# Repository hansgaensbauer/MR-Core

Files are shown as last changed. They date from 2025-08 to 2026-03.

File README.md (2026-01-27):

### __Quick Start:__ The [software](/software) folder contains a template Jupyter Notebook and documentation for the MRC class. 

# MR-Core
An FPGA Driven DAC + ADC for Magnetic Resonance, intended as a capable controller for Magnetic Resonance Imaging and Magnetic Resonance Relaxometry. 

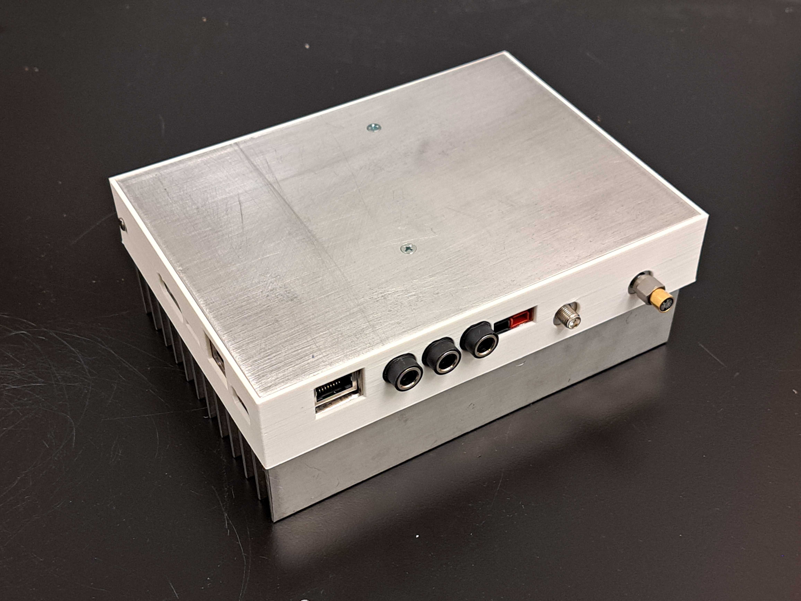
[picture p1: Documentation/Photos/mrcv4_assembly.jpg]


### Features
- STM32F767 Microcontroller for experiment-level sequencing and backend signal processing
- Artix 7 FPGA for pulse generation, digital downconversion and DSP
- 500MSps dual oversampling DAC with on-chip NCO for RF pulse synthesis
- 120MSps dual ADC
- X, Y, and Z gradient drivers for 3A low impedance gradient coils
- 5Gbps USB-3.0 controller for raw data extraction
- 100/10 Ethernet 
- SD Card Interface
- Magnet/switch interface for temperature control and T/R switching

# User Manual

## Repository Setup and Software Prerequisites
### Required Software
- [KiCAD EDA](https://www.kicad.org/)
- [STM32CubeIDE](https://www.st.com/en/development-tools/stm32cubeide.html)
    - [STM32CubeF7 Package](https://www.st.com/en/embedded-software/stm32cubef7.html) Version 1.7.1 or 1.7.2
    - ARM CMSIS 5.4.0
- [AMD Vivado](https://www.xilinx.com/products/design-tools/vivado.html)

</br>
To set up the KiCAD Libraries:

- Open KiCAD, go to Preferences -> Configure Paths..., and add a new Environment Variable called "BioMEMS" that points to the hardware/Library folder. 
- Add the symbol library by selecting Preferences -> Manage Symbol Libraries... and selecting the BioMEMS.kicad_sym file in this folder. 
- Check that the library path shows up as "${BioMEMS}.kicad_sym". 
- Add the footprint library by selecting Preferences -> Manage Footprint Libraries... and selecting the BioMEMS.pretty folder in Library. 
- Check that the library path uses the ${BioMEMS} variable.

</br>
The STM32CubeIDE project requires similar setup:

- Create an environment variable called STM32CUBE_REPO, pointed to the STM32Cube\Repository folder on your computer.
- Restart your computer
- Open the project in STM32CubeIDE, and navigate to the IOC file
- Under "Software Packs", click "Manage Software Packs"
- Click "From URL", then "New"
- Add the URL "https://raw.githubusercontent.com/STMicroelectronics/STM32CubeF7/master/Drivers/CMSIS/ARM.CMSIS.pdsc"
- Click "OK" (several times) to add the software pack.
- You may have to close and reopen the "Manage Software Packs" window
- Click the "ARM" tab, and check "CMSIS 5.4.0"
- Click "OK" to close the window, then click "Select Components" under "Software Packs"
- Expand ARM.CMSIS, and check "CMSIS Core - 5.1.2" and "CMSIS DSP 1.5.2" 
- Click OK
- Under Middleware and Software Packs, click "CMSIS", and make sure both CMSIS Core and DSP are checked in the panel that opens
- Save the IOC and rebuild the code
- To add the STM32CubeF7 repository, extract the STM32CubeF7 to the STM32CUBE_REPO folder (next to "Packs")
- Pull the STM32Cube_FW_F7_V1.17.X folder out so it's at the same level as the Packs folder. Check that the path to this folder matches the include paths in Project->Properties (you may have to rename the folder or adjust the paths).

## Hardware Description
### Open Assembly
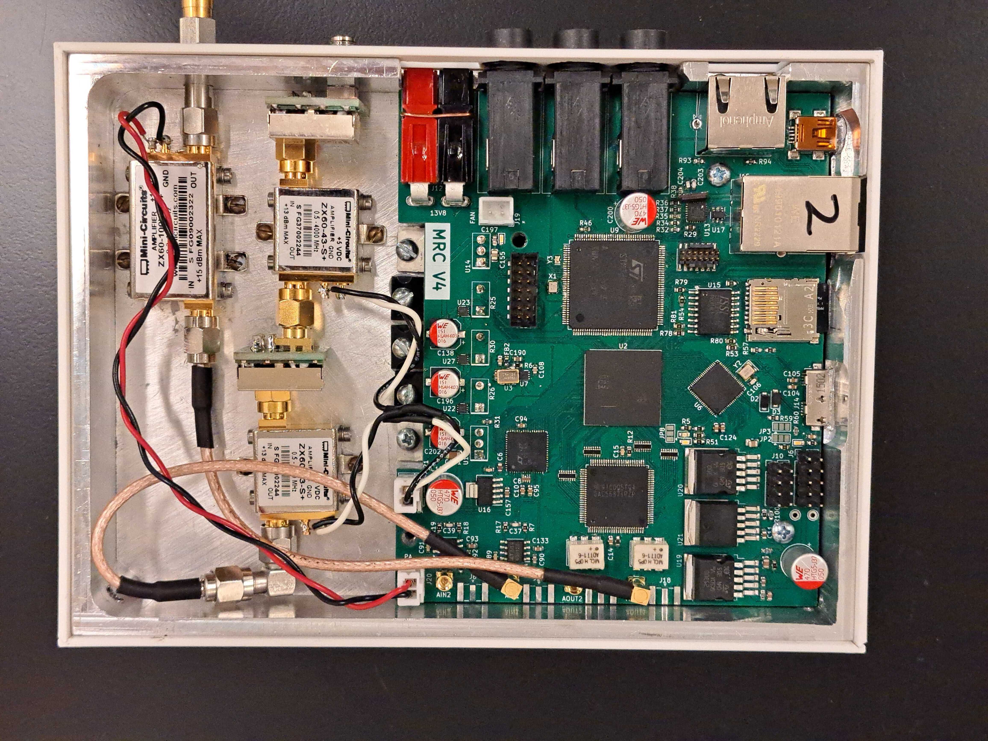
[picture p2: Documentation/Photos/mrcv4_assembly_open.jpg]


### PCB Connector Diagram
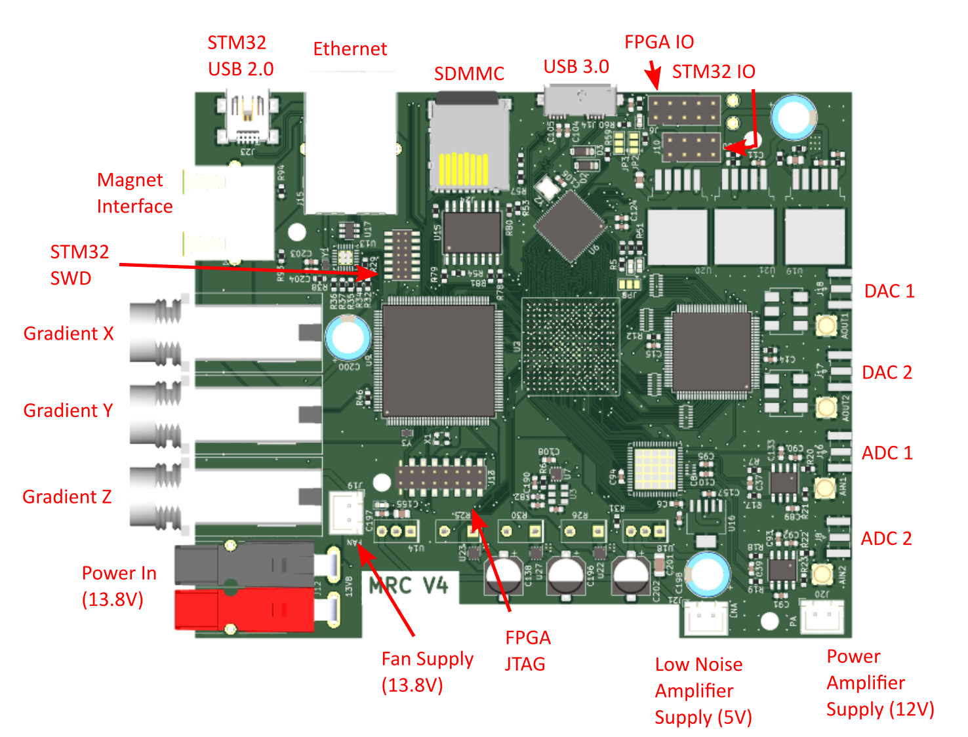
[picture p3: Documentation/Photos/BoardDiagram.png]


## Powering On
The MR-Core is designed to work with a 13.8V DC power supply, such as those sold by [Astron Corporation](https://www.astroncorp.com/). These are commonly used for amateur radio, but any linear power supply capable of providing 10A continuously is suitable. If the gradients are not used, only 3A are required. The power connector is a [ASMPR45-1X2-RK](https://www.digikey.com/en/products/detail/anderson-power-products-inc/ASMPR45-1X2-RK/13150596) from [Anderson Power Products, Inc.](https://www.andersonpower.com/us/en.html).

## Programming
### Programming the Microcontroller
- Connect an ST-Link programmer to the STM32 SWD port on the MRC. 
- Flash using STM32CubeIDE

### Programming the FPGA
- Connect an AMD compatible JTAG cable to the FPGA JTAG port on the MRC.
- Open the Hardware Manager in Vivado
- Click "Auto Connect"
- Click "Program" and select the .bit file for the FPGA

### Programming the SPI Flash
By default, new designs programmed into the FPGA must be reprogrammed every time the device loses power. To allow the FPGA image to persist between reboots, a SPI configuration flash is included that can program the FPGA with a default image on startup. To change this default image:
- Right click on create bitstream
- Click "bitstream settings"
- Check the ".bin" option
- Click Apply
- Generate the bitstream
- Click "Add Configuration Memory Device"
- If prompted, search for and select "IS25LP256"
- Right click on the device
- Click "Program"
- find .bin file in runs->impl_1 folder
- Select "Pull-Ups"
- Select the "Erase", "Program", and "Verify" options
- Select Apply, OK
- Disconnect the programming cable and restart the FPGA.

To program the SPI flash without changing the configuration (which you will want to do in most cases to update the FPGA image), the steps are more simple.
- In the Hardware Manager, right click on the SPI Flash in the Hardware window.
- Click "Program Configuration Memory Device"

## Analog Frontend (AFE)
The AFE for the MRC consists of two SXLP-21.4+ lowpass filters and two ZX60-43-S+ gain block amplifiers for the receive side, and one ZX60-100VHX+ amplifier for transmit. The amplifiers are powered by connectors from the MRC PCB, and should not be used with the heatsink removed. The transmit amplifier may be destroyed if it transmits into a poorly tuned or disconnected probe. For development, the transmit port of the MRC should be connected to a 50 ohm termination. The filters can be bypassed by soldering an 0603 resistor onto the jumpers on the filter PCBs. The MRC AFE is intended to be used with an external switch and preamplifier located on the probe - the gain blocks are not low noise amplifiers. 

## Magnet Interface
The magnet interface is connected to the MRC using an ethernet cable. The interface exposes FPGA IO for switching, as well as 3.3V power and microcontroller IO for general use. 

## Gradients
The gradients use 1/4" TRS audio connectors. Do not use 1/4" mono connectors, and do not insert or remove the connectors for the gradients when the board is powered. Doing so can damage the gradient drivers. The gradients are driven by H-bridge circuits to the supply voltage, current limited to 3A by three power resistors on the board. For this reason, neither contact for the gradients (Tip or Ring) is grounded. The Shield should not be connected to the gradient coil.

## USB 3.0
Support for direct baseband sample streaming with Steam-O-Scope firmware from [Joseph Feld](https://github.com/JosephFeld).

## Switch/Preamplifier Module
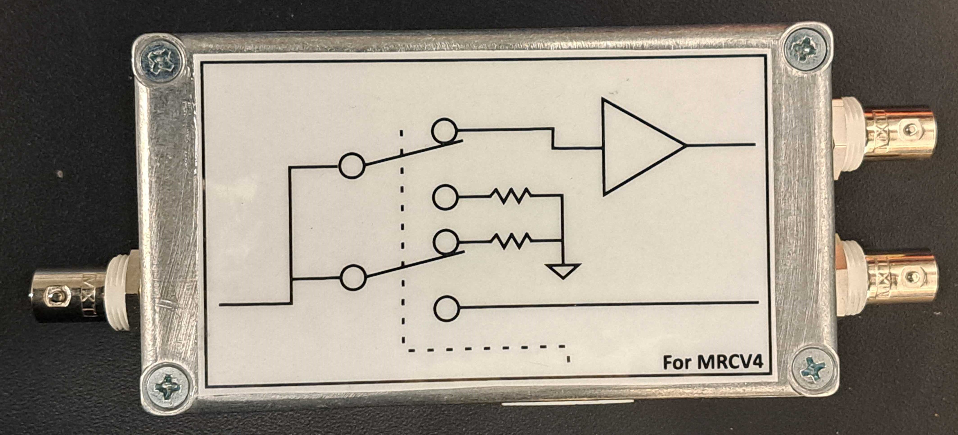
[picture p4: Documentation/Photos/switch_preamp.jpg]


In order to make it possible to use non-MRC compatible probes with the MRC, a switch and preamplifier module is provided. This module provides about 10dB of gain and it includes a ZX80-DR230-S+ absorbtive RF switch. The truth table for the switch is:
| SW[1]  | SW[0] | Switch State |
| ------------- | ------------- | ----- |
| 0  | 0  | Both Off |
| 0  | 1  | Receive |
| 1  | 0  | Transmit |
| 1  | 1  | Unknown |

The yellow LED on the preamplifier module ethernet connector indicates the status of the transmit switch (on = closed) and the green LED likewise indicates the status of the receive switch.

## MRR-Core Image
This image implements a general purpose, programmable controller for MRI sequences. 

The system is programmed by the STM32 over SPI, and each SPI transaction is 16 bits with the MSB first. There are three types of SPI command: control register programming, frequency tuning word programming, and sequence programming. 

The control register is used for general purpose control of the FPGA, and can be accessed with a SPI transaction where bits [15:14] are `0b10`. The 8 LSBs give the new control register value. The control register is shown below:
**CMD (Opcode `0b00`)**
```
[  7  |  6  |  5  |  4  |  3  |  2  |  1  |  0  ]
[ RST |     |     |     |     |     |TRIG |     ]
```

To program the 16 bit frequency tuning word, the system must first be put into frequency tuning mode by sending the frequency tuning command `0xC000`. The frequency tuning word is sent on the next transaction, and the system will automatically return to IDLE afterward.

To enter sequence programming, the sequence programming command must be sent with the number of lines in the sequence program. The programming command starts with `0b00`, and the 14 LSBs are the number of 16 bit instructions in the sequence.

### MRC Instruction Set
The MRC uses a very simple instruction set designed for precise execution of any pulse sequences. There are four instructions:

**CMD (Opcode `0b00`)**
```
[ 15 | 14 | 13 | 12 | 11 | 10 |  9 |  8 |  7 |  6 |  5 |  4 |  3 |  2 |  1 |  0 ]
[  0 |  0 |   AMP   |  PHASE  |   GRX   |   GRY   |   GRZ   |      RESERVED     ]
```
Change the transmitter amplitude and phase to the values indexed by AMP and PHASE. Set the gradients to the values set by GR[xyz].

**LSET (Opcode `0b01`)**
```
[ 15 | 14 | 13 | 12 | 11 | 10 |  9 |  8 |  7 |  6 |  5 |  4 |  3 |  2 |  1 |  0 ]
[  0 |  1 | COUNTER |                          VALUE                            ]
```
Set COUNTER to VALUE.

**JMP (Opcode `0b10`)**
```
[ 15 | 14 | 13 | 12 | 11 | 10 |  9 |  8 |  7 |  6 |  5 |  4 |  3 |  2 |  1 |  0 ]
[  1 |  0 | COUNTER |                         ADDRESS                           ]
```
If COUNTER is not zero, jump to the absolute ADDRESS. If COUNTER is zero, set COUNTER to `0xFFFF` and advance the instruction counter.

**HALT (Opcode `0b11`)**
```
[ 15 | 14 | 13 | 12 | 11 | 10 |  9 |  8 |  7 |  6 |  5 |  4 |  3 |  2 |  1 |  0 ]
[  1 |  1 |                                                                     ]
```
Terminates the sequence.

To better compress the immediates for programming amplitude and phase so that all of the pulse parameters can be updated simultaneously, the AMP and PHASE fields in the CMD instruction do not directly specify the amplitude or phase, but instead give the address of the correct value within separate lookup tables that are programmed with the sequence. The first four lines of the sequence program are the four amplitude fields, and the second four lines are the four phase fields. 

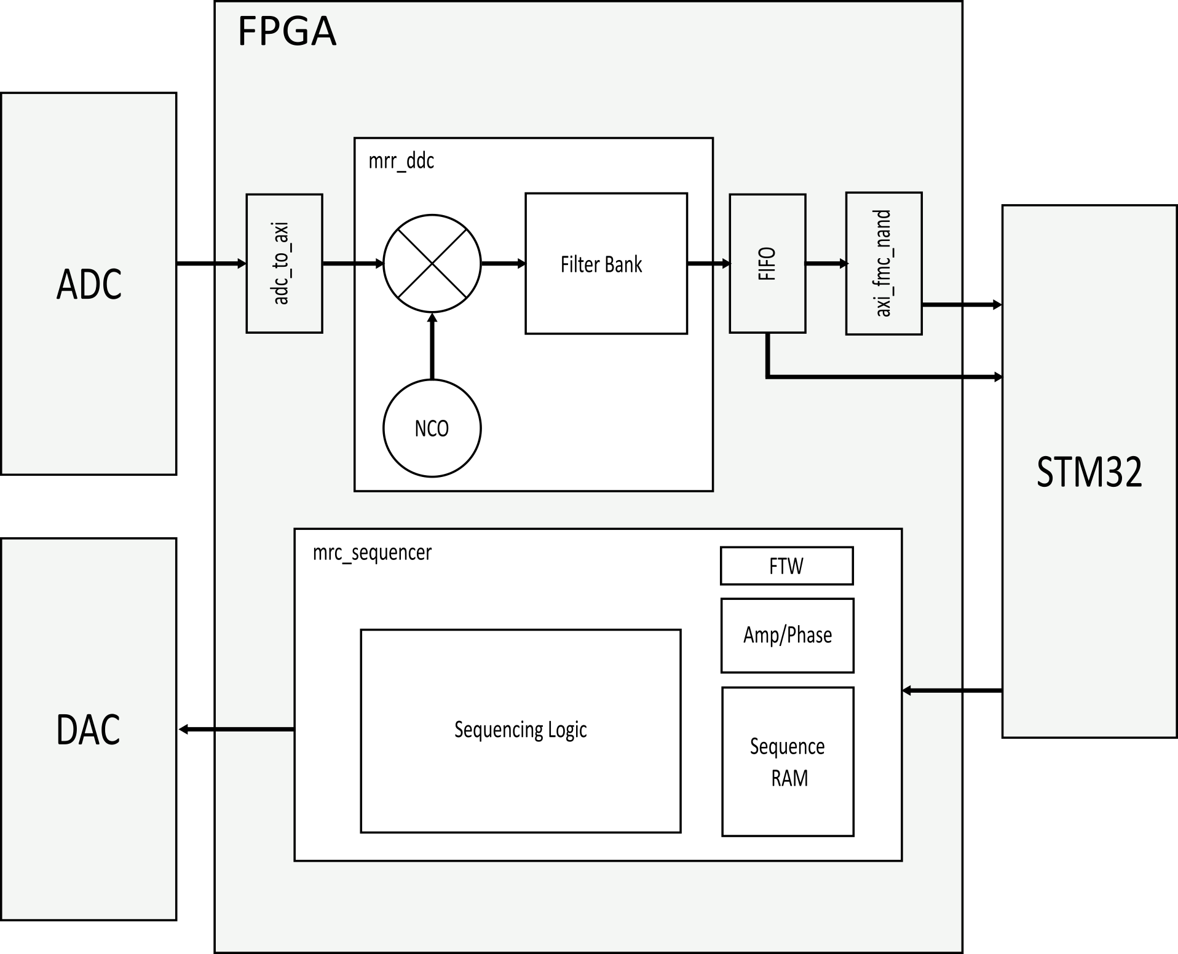
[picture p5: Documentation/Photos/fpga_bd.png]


### Digital Downconversion
The 120MSps data stream from the ADC is too much data for the STM32 to process, and most of this data is useless as it covers frequencies far away from the Larmor frequency of the magnet. To lower the data rate and isolate only a certain band of interest, the FPGA can digitally downconvert and downsample the ADC data stream. The digital design responsible for this is contained in the "mrr-ddc" block design within the MR-Core Vivado project. 

The structure of the DDC is shown in the HDL block diagram above. The parallel data is converted to AXI by the adc_to_axi module. This is fed into the mrr-ddc block design, which includes a complex multiplier and direct digital synthesizer for downconversion. The frequency shifted products are filtered and passed to a FIFO, before being passed to the STM32 using the STM32 Flexible Memory Controller (FMC).

The layout of the digital filter is shown below:

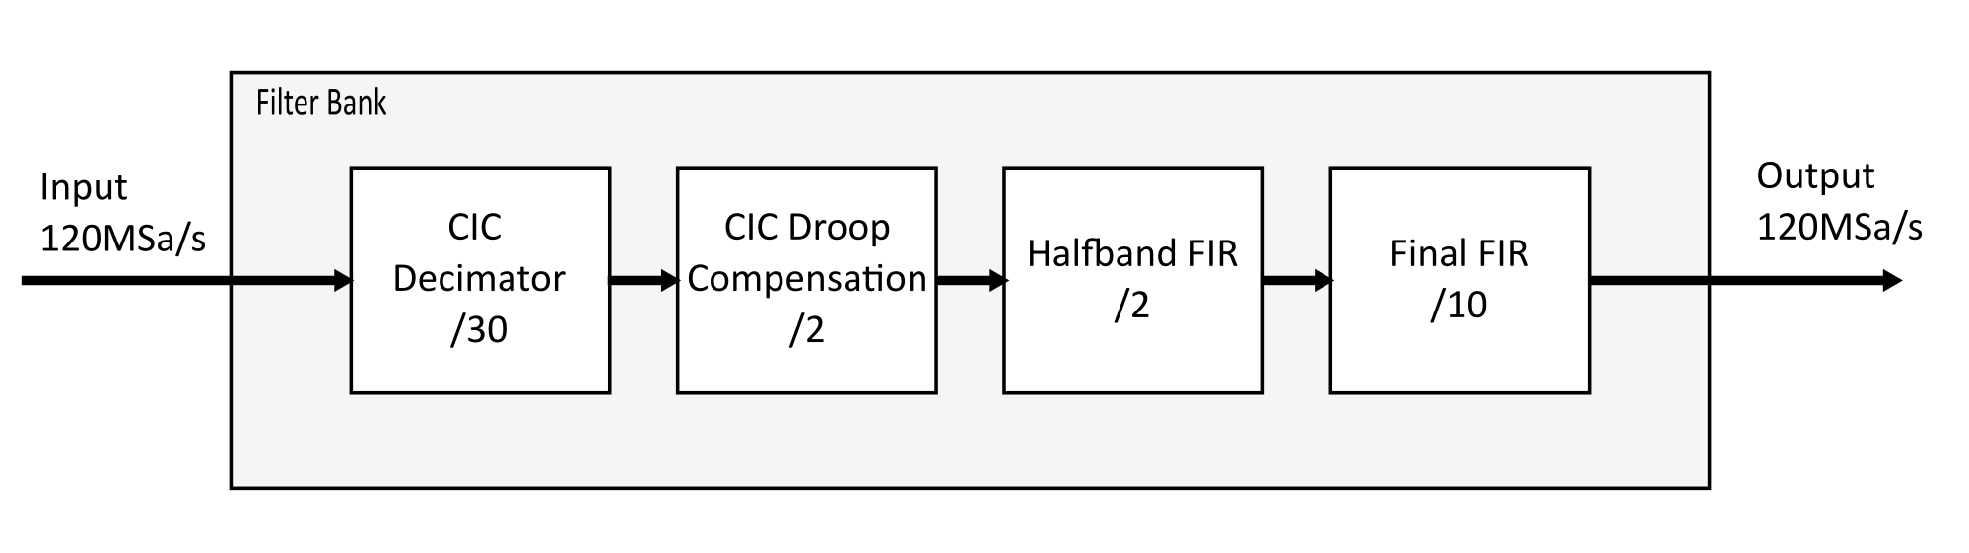
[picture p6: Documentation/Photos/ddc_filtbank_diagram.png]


This filter is responsible for both decimation and the bulk of noise rejection, so the performance requirements are strict. The filter is implemented in several stages so that the high complexity FIR filters at the end see only data streams that are already significantly decimated (the final FIR filter sees an input data rate of 1MSa/s, compared to 120MSa/s for the CIC decimator).

The filter design is done in Matlab, and the current design is captured by filtdesign.m in MR-Core->hdl->Utilities. The transfer function is shown below (x axes in MHz):

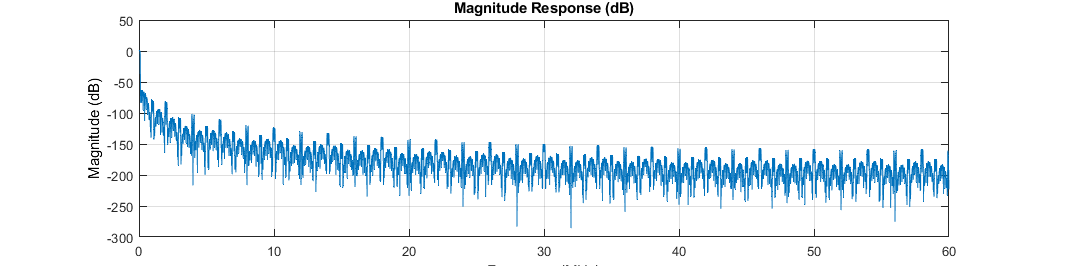
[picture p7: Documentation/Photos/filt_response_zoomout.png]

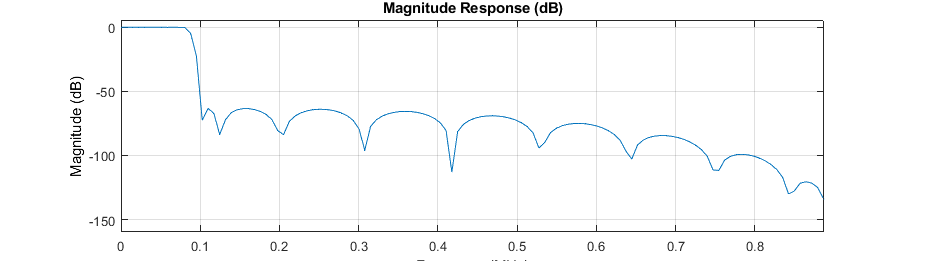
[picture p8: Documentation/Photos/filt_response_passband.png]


## Firmware
The firmware running on the STM32 is responsible for processing or passing the data stream from the FPGA during receive, and also for configuring the FPGA, the DAC, and the ADC. The mrc STM32CubeIDE project in the "firmware" folder provides C drivers for the DAC, the ADC, and an "MRC" driver that handles communication with the FPGA, pulse sequencing, and data streaming. The DAC and ADC drivers provide access to the test patterns, power down states, and programming registers for these chips.

For USB 2.0 Full speed data streaming, the `Transfer_Buffer()` function in mrc.c will coordinate FMC reads into a ping-pong buffer that is then emptied over the USB CDC hardware into a PC. A basic serial command interface is available in this demo so that a user can trigger pulse-echo sequences by sending the command `pulseecho` over USB CDC.

## Software and UI
### Pulseq Compiler
A limited Pulseq compiler is provided in `software`. This program requires pypulseq to run, however, the latest stable release of pypulseq cannot run with the most recent versions of numpy. This can be solved by replacing every instance of `np.float` and `np.complex` in the sigpy and pypulseq libraries with `float` and `complex` respectively. 

To run the compiler, use `py mrc_pulseq_assembler.py [sequence_file.seq]` where `[sequence_file.seq]` is replaced by the path to your pulseq file. This will generate a .mrc file with the machine code for the MRI. To facilitate debugging, a objdump-style disassembler is also provided. To run the disassembler, use `py mrcdump.py [mrc_file.mrc]` where `[mrc_file.mrc]` is replaced with the path to your .mrc file. It will produce an output in the following format:

```
Statics:
Phase 0: 0
Phase 1: 0
Phase 2: 0
Phase 3: 0

Amp 0: 0
Amp 1: 28000
Amp 2: 56000
Amp 3: 0

Instructions:
0:      0001000000000000        cmd     1 0 00 00 00
1:      0100010010101111        lset    0 1199
...     ...                     ...     ...
20:     0000000000000000        cmd     0 0 00 00 00
21:     1100000000000000        halt.
```

For the system demo, a python driver for the MRC board is available in the "software" folder. bioreactormonitoring.py uses this driver to periodically acquire pulsecho sequences and plot the received data and extracted T2 values on an animated graph on the computer.

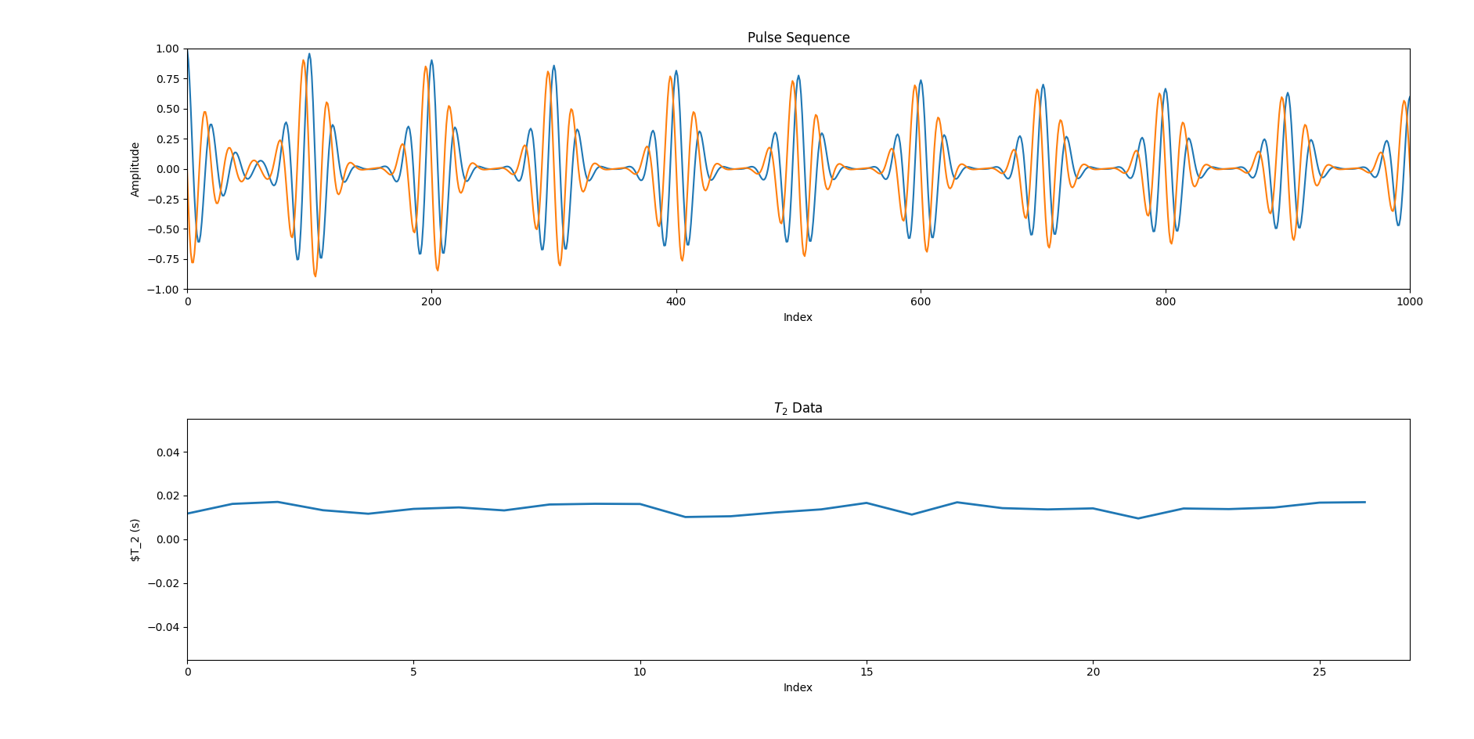
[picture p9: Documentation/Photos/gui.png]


## Contributing
Best practices: make your own branch!

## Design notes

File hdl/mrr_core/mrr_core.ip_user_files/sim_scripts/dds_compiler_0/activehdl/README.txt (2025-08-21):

################################################################################
# Vivado (TM) v2024.1 (64-bit)
#
# README.txt: Please read the sections below to understand the steps required to
#             run the exported script and how to fetch design source file details
#             from the file_info.txt file.
#
# Generated by export_simulation on Sun Aug 25 01:28:21 -0400 2024
#
################################################################################

1. Steps to run the generated simulation script

From the shell prompt in the current directory, issue the following command:-

./dds_compiler_0.sh

This command will launch the 'compile', 'elaborate' and 'simulate' functions
implemented in the script file for the 3-step flow. These functions are called
from the main 'run' function in the script file.

The 'run' function first calls the 'check_args' function, the purpose of which
is to verify the generated script arguments and print error if incorrect switch
is specified. The 'run' function then calls the 'setup' function, the purpose of
which is to specify custom or initialization commands. The function also executes
following sub-functions:-
'reset_run' if -reset_run switch is specified.
'reset_log' if -reset_log switch is specified.

The purpose of 'reset_run' function' is to delete the simulator generated design
data from the previous run and the purpose of 'reset_log' function' is to delete
the simulator generated log files.

The 'run' function then calls the 'init_lib' function, the purpose of which is to
create design library mappings and directories. This function is called before the
'compile' step. By default, if '-step' switch is specified with the script then the
script will execute that specfic step, else it will execute all steps applicable
for the target simulator.

For more information on the script, please type './dds_compiler_0.sh -help'

2. Design source file information

export_simulation generates a 'file_info.txt' file that contains design file information
based on the compile order when export_simulation was executed from Vivado. The file
contains information about the file name, type, library it is compiled into, whether
it is part of the IP, associated library, file path information in a comma separated
format. This file can be parsed to extract the required information for generating a
custom script or can be read from verification test infra.

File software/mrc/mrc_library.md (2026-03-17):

# MRC Python Library
The following is documentation for the MRC python library, which includes drivers for the MRC hardware, as well as built-in pulse sequence creation tools and post processing functions for magnetic resonance experiments. 

# Class: `Console`
This class encapsulates functions that interact with the MRC hardware. 

## Attributes

- **`rx_data`**: (numpy.ndarray of numpy.complex128) – This array stores the most recent raw received data. The sample rate is 100kSa/s.
- **`ser`**: (pyserial.Serial) – Serial object for communicating with the console.
- **`frequency`**: (int) – This is the console center frequency. This variable should not be set externally, and is only used for data post-processing. Instead, use Console.freq() to change the system frequency. 

## Methods

### `Console(port = None, frequency = 21.65e6) -> None`
Connect to and initialize the MRC console. This is the constructor for the MRC class.

**Parameters:**
- **`port`**: (str) – Optional COM port of the system. If no port is provided, the class will attempt to autodetect the console.
- **`frequency`**: (float) – Calibration center frequency for the system. This should be within 100kHz of the true magnet frequency.

### `Console.amp(amplitude) -> None`
Set the system transmit amplitude. 

**Parameters:**
- **`amplitude`**: (float) – The system coil strength in units of DAC Counts/Hz. This value will be multiplied by the pulse amplitude defined in the pulseq experiment, which has units of Hz. The maximum DAC output is 2<sup>15</sup>, so the product of the system coil strength and the pulse amplitude must fall below this number.

### `Console.freq(frequency) -> None`
Sets the system Larmor frequency in Hz.

**Parameters:**
- **`frequency`**: (int) – The current larmor frequency. 

### `Console.run(sequence = None) -> None`
Load and run the provided sequence, or run the currently loaded sequence. 

**Parameters:**
- **`sequence`**: (str or Sequence, optional) – If `sequence` is provided, it will be loaded onto the console before the experiment is triggered. If it is not provided, then the console will run the last sequence loaded. If `sequence` is str, it represents the path to a compiled sequence file. If `sequence` is type `pypulseq.Sequence.sequence.Sequence`, this function will compile it into a temporary file, load it onto the system, and then delete the temporary file.

### `Console.calibrate(calibrate_freq=True, calibrate_flip_angle=False) -> Tuple`
Perform frequency and flip angle calibration. The use of this function to calibrate the flip angle is not recommended - in most cases, the system coil strength should be set manually for each new probe and then held constant. This function will update the system frequency and amplitude automatically if the corresponding calibration is requested. It loads a spinecho experiment to perform calibration, so it is necessary to reload the desired experiment after performing calibration.

**Parameters:**
- **`calibrate_freq`**: (bool) – If `calibrate_freq` is true, this function will run an FFT based frequency calibration.
- **`calibrate_flip_angle`**: (bool) – If `calibrate_flip_angle` is true, this function will run an amplitude calibration.

**Returns:**
- **`f0, coil_strength`**: (tuple) – The calculated Larmor frequency and coil strength after calibration. If either calibration was not performed, the corresponding return value will be `None`.

### `Console.run_cpmg(n_echoes = 100, echo_time = 3e-3, t90 = 200e-6, t180 = 200e-6) -> Tuple`
Builds, loads, and runs a Carr-Purcell-Meiboom-Gill experiment. 

**Parameters:**
- **`n_echoes`**: (int) – The number of echoes in the experiment.
- **`echo_time`**: (float) – The inter-echo spacing in seconds.
- **`t90`**: (float) – The duration of the 90 degree pulse in seconds.
- **`t180`**: (float) – The duration of the 180 degree pulse in seconds.

**Returns:**
- **`echo_time_points, echo_amplitudes`**: (tuple) – The time coordinates and amplitudes of the echoes from the CPMG experiment.

### `Console.run_ir(inversion_time, n_echoes = 100, echo_time = 3e-3, t90 = 200e-6, t180 = 200e-6) -> Tuple`
Builds, loads, and runs an inversion-recovery CPMG experiment. 

**Parameters:**
- **`inversion_time`**: (float) – The inversion time for the experiment in seconds.
- **`n_echoes`**: (int) – The number of echoes in the experiment.
- **`echo_time`**: (float) – The inter-echo spacing in seconds.
- **`t90`**: (float) – The duration of the 90 degree pulse in seconds.
- **`t180`**: (float) – The duration of the 180 degree pulse in seconds.

**Returns:**
- **`echo_time_points, echo_amplitudes`**: (tuple) – The time coordinates and amplitudes of the echoes from the IR CPMG experiment.

### `Console.run_ir_t1(inversion_times, n_echoes = 100, echo_time = 3e-3, t90 = 200e-6, t180 = 200e-6, inter_experiment_delay = 3) -> Tuple`
Measures T<sub>1</sub> using repeated IR CPMG experiments with user specified inversion times.

**Parameters:**
- **`inversion_time`**: (numpy.ndarray) – An array of inversion times to sweep.
- **`n_echoes`**: (int) – The number of echoes in the experiment.
- **`echo_time`**: (float) – The inter-echo spacing in seconds.
- **`t90`**: (float) – The duration of the 90 degree pulse in seconds.
- **`t180`**: (float) – The duration of the 180 degree pulse in seconds.
- **`inter_experiment_delay`**: (float) – The wait time between each experiment in seconds.

**Returns:**
- **`initial_magnetizations`**: (numpy.ndarray) – The initial magnetizations for each inversion time specified in the input arguments. 

### `Console.load(sequence) -> None`
Loads a pypulseq Sequence or cpmpiled .mrc file onto the system.

**Parameters:**
- **`sequence`**: (str or Sequence) – If `sequence` is str, it represents the path to a compiled sequence file. If `sequence` is type `pypulseq.Sequence.sequence.Sequence`, this function will compile it into a temporary file, load it onto the system, and then delete the temporary file.

### `amp(amplitude) -> None`
Sets the system coil B<sub>1</sub> strength in DAC Counts/Hz.

# Other Functions
These functions are not part of the Console class, and should be called with `mrc.[functionname]()`

### `build_spinecho(te, t90, t180) -> pypulseq.Sequence.sequence.Sequence`
Convenience function for creating a pulseq spin-echo sequence.

**Parameters:**
- **`te`**: (float) – The inter-echo spacing in seconds.
- **`t90`**: (float) – The duration of the 90 degree pulse in seconds.
- **`t180`**: (float) – The duration of the 180 degree pulse in seconds.

**Returns:**
- **`sequence`**: (pypulseq.Sequence.sequence.Sequence) – A spin-echo experiment implemented in pypulseq.

### `build_cpmg(echo_time, num_echoes, t90, t180) -> pypulseq.Sequence.sequence.Sequence`
Convenience function for creating a pulseq CPMG sequence.

**Parameters:**
- **`echo_time`**: (float) – The inter-echo spacing in seconds.
- **`num_echoes`**: (int) – The number of echoes in the experiment.
- **`t90`**: (float) – The duration of the 90 degree pulse in seconds.
- **`t180`**: (float) – The duration of the 180 degree pulse in seconds.

**Returns:**
- **`sequence`**: (pypulseq.Sequence.sequence.Sequence) – A CPMG experiment implemented in pypulseq.

### `build_ir(inversion_time, echo_time, num_echoes, t90, t180) -> pypulseq.Sequence.sequence.Sequence`
Convenience function for creating a pulseq inversion recovery CPMG sequence.

**Parameters:**
- **`inversion_time`**: (float) – The inversion time in seconds.
- **`echo_time`**: (float) – The inter-echo spacing in seconds.
- **`num_echoes`**: (int) – The number of echoes in the experiment.
- **`t90`**: (float) – The duration of the 90 degree pulse in seconds.
- **`t180`**: (float) – The duration of the 180 degree pulse in seconds.

**Returns:**
- **`sequence`**: (pypulseq.Sequence.sequence.Sequence) – An inversion recovery CPMG experiment implemented in pypulseq.

### `get_echo_amplitudes(rx_data, num_echoes, te, t90) -> numpy.ndarray`
Extract the echo amplitudes from the received data

**Parameters:**
- **`rx_data`**: (np.ndarray of numpy.complex128) – The received data from a CPMG experiment
- **`num_echoes`**: (int) – The number of echoes in the experiment.
- **`te`**: (float) – The inter-echo spacing in seconds.
- **`t90`**: (float) – The duration of the 90 degree pulse in seconds.

**Returns:**
- **`mags_abs`**: (np.ndarray) – The CPMG echo amplitudes.

### `get_t2(echo_data, te) -> float`
Estimate T<sub>2</sub> from an array of echo amplitudes.

**Parameters:**
- **`echo_data`**: (np.ndarray) – Array of echo amplitudes.
- **`te`**: (float) – The inter-echo time in seconds.

**Returns:**
- **`t2`**: (float) – The best-fit value for T<sub>2</sub>.

### `get_m0(echo_data, te) -> float`
Estimate M<sub>0</sub> from an array of echo amplitudes.

**Parameters:**
- **`echo_data`**: (np.ndarray) – Array of echo amplitudes.
- **`te`**: (float) – The inter-echo time in seconds.

**Returns:**
- **`m0`**: (float) – The best-fit value for M<sub>0</sub>.

### `compile_sequence(sequence, progfile) -> None`
Compile a pypulseq sequence or .seq file into a .mrc binary for the system.

**Parameters:**
- **`sequence`**: (str or pypulseq.Sequence.sequence.Sequence) – If `sequence` is str, it represents the path to a compiled sequence file. If `sequence` is type `pypulseq.Sequence.sequence.Sequence` it will be compiled without being saved as a .seq file first.
- **`progfile`**: (str) – The path for the .mrc file that will be produced.

### `mrcdump(mrcfile) -> None`
Disassemble a .mrc file and pretty-print the result.

**Parameters:**
- **`mrcfile`**: (str) - The path to the .mrc file to disassemble. 

# Building the Library

1. Update pyproject.toml
2. Build the class:
```
cd \software\mrc
py -m buid
```
3. Install the class
    1. Copy the wheel from `mrc\dist` to wherever is convenient for install
    3. `%pip install mrc-X.X.X-py3-none-any.whl` to install (change to whatever the right path is)

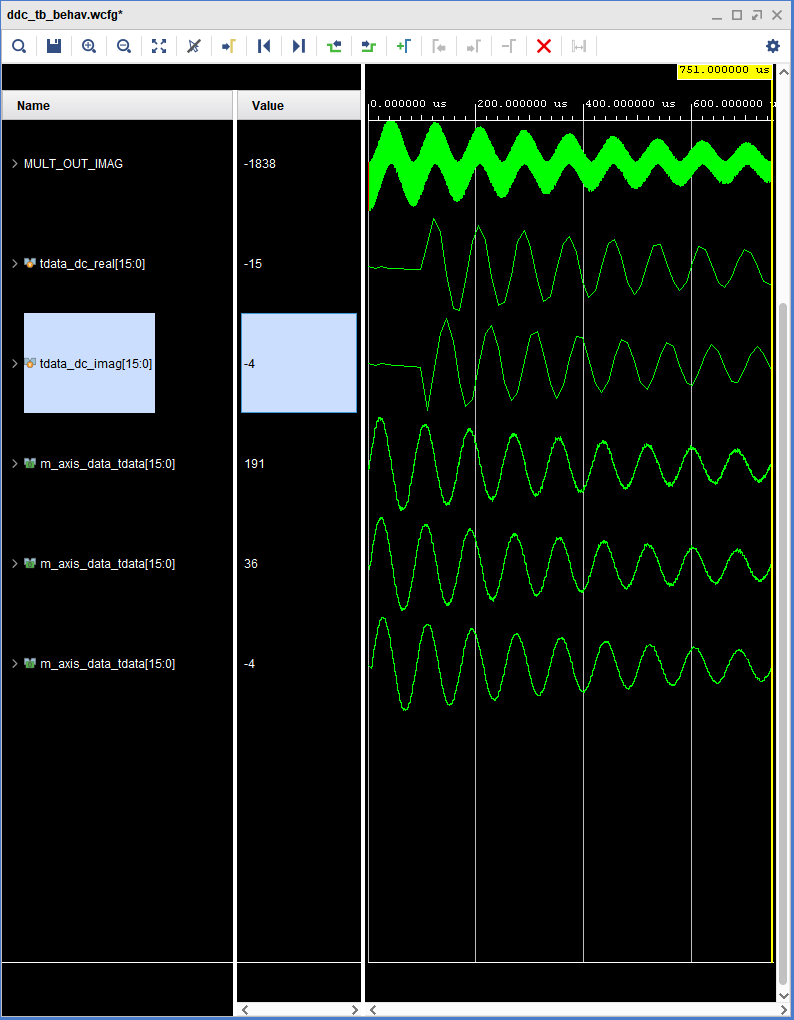
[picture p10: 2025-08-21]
Documentation/Photos/FullFilterSim.png

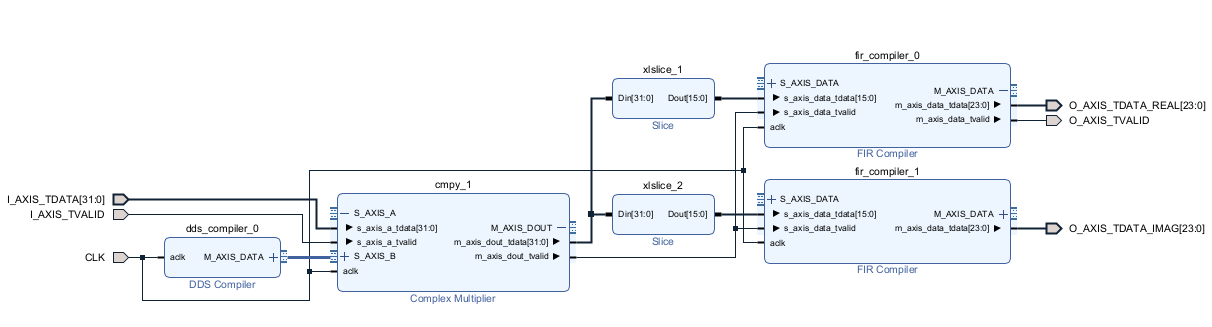
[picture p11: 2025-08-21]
Documentation/Photos/DDC_BD.png

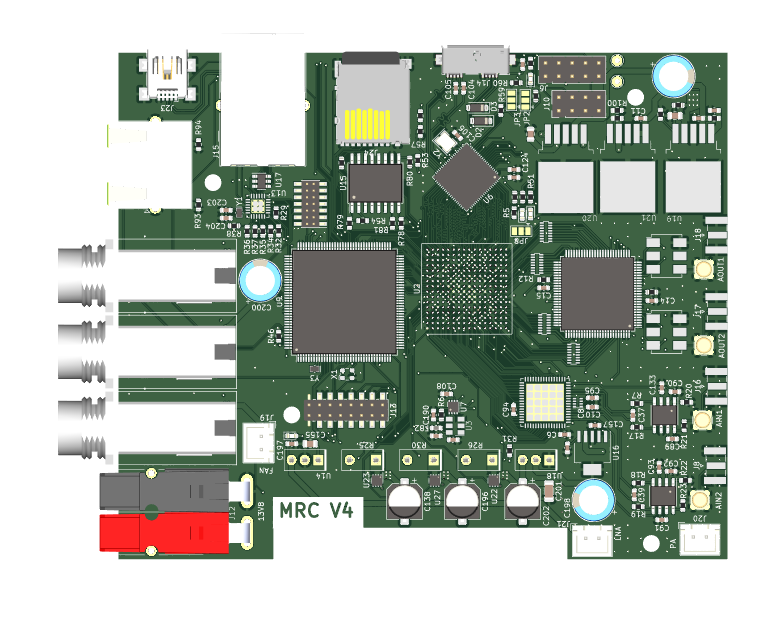
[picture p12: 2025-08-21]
Documentation/Photos/MRCV4_PCB_Render.png

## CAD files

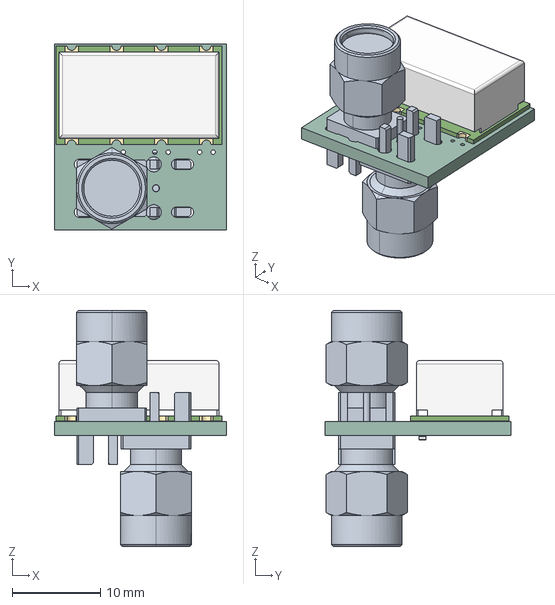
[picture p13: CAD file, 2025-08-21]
hardware/MRR-AFE/filt2/filt2.step
19.5 x 21.0 x 26.7 mm
filt2 PCB

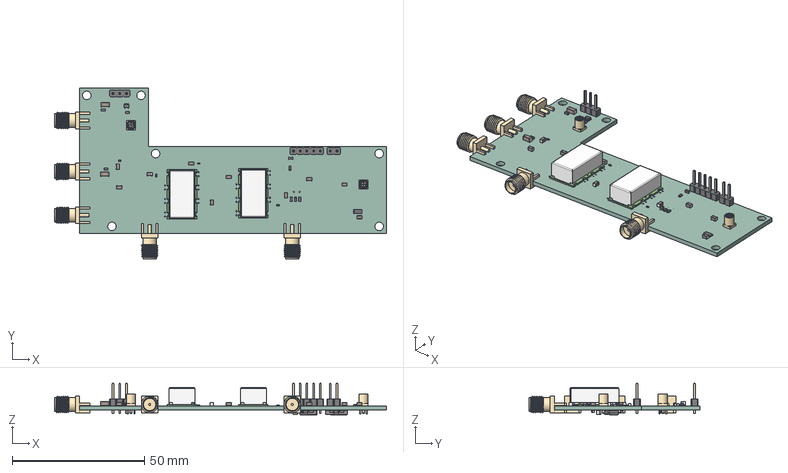
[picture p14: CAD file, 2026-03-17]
hardware/MRR-AFE/mc3_afe/mc3_afe.step
125.5 x 64.5 x 11.9 mm
MMCX_Molex_73415-1471_Vertical x 2
R_0603_1608Metric x 3
SMA_Samtec_SMA-J-P-H-ST-EM1_EdgeMount x 5
R_1206_3216Metric
C_0805_2012Metric x 10
SOT_353_SC_70_5
R_0402_1005Metric x 4
C_0603_1608Metric x 9
C_1206_3216Metric x 6
PinHeader_1x05_P254mm_Vertical
PinHeader_1x02_P254mm_Vertical
PinHeader_1x03_P254mm_Vertical
SOT_223 x 2
_autosave-mc3_afe_PCB

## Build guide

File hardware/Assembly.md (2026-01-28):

# Assembly Guide

## Attaching the MRC Board to the Heatsink
Both designs are designed to have all of the hardware components mounted on a heatsink (Wakefield Thermal 125325). 

The MRC board is attached with 4-40 standoffs, and the gradient current limiting resistors and linear regulators need to be attached to the bottom of the MRC board so that they can be bolted to the heatsink. In practice, the easiest way to get the height right is to solder the resistors and regulators only after everything is bolted together.

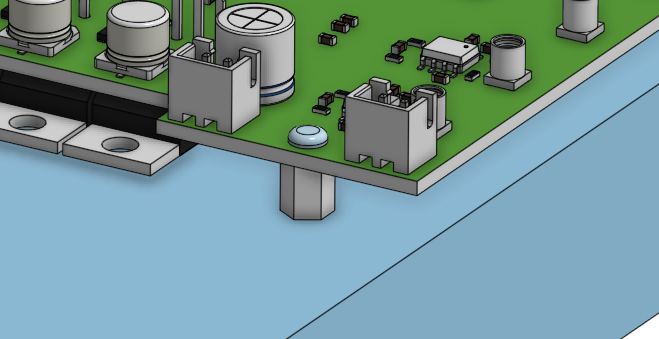
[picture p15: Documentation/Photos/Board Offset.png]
The position of the resistors and regulators on the heatsink


## Frontends

The main MR-Core PCB does not include an analog frontend, so that the ADC/DAC board can be used with a variety of frontends suited for different purposes. 

This repository includes two example frontends that can be used for low power experiments or as a first stage for larger power amplifiers. The first design uses connectorized components from Mini-Circuits, the second (currently only in the 96wp branch) is integrated and includes a programmable attenuator and a T/R switch. 

### Connectorized Frontend

The mechanical designs for the first frontend can be found here: [MRC-ASSY-V3 Onshape](https://cad.onshape.com/documents/08d5cc469933dcf1f3680b8f/w/019d42becb6093bd4138e05a/e/b85e3df62a5811d6b4cc045a?renderMode=0&uiState=6979326bf122fc4615e7638b)

In addition to the two filter boards in the MRR-AFE folder, the following connectorized components are required:

- ZX60-100VH+
- C-2081888-1
- 2x ZX60-3018G-S+

### MRC-AFE Frontend

The mechanical designs for the second frontend can be found here: [MRC3_Case Onshape](https://cad.onshape.com/documents/a6a315e3a86249716985f9ad/w/217173f5852425dc1e41f329/e/d7597495945d9f2bb802a412?renderMode=0&uiState=697932bb78f8488f172080e4). The PCB design files and BoM for the AFE are currently only in the 96wp branch.

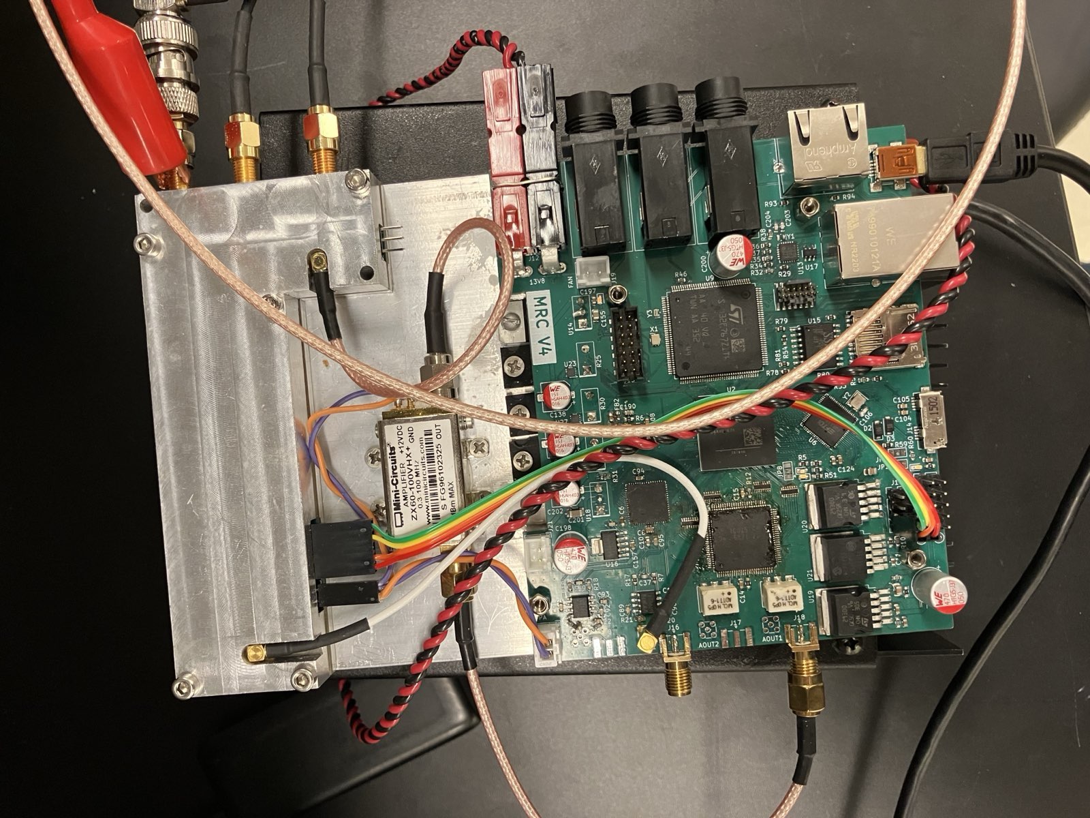
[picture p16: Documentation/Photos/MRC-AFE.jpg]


The AFE board is supported by two aluminum shields. The shields are designed to be straightforward to machine, and the designs can be found in the Onshape linked above.

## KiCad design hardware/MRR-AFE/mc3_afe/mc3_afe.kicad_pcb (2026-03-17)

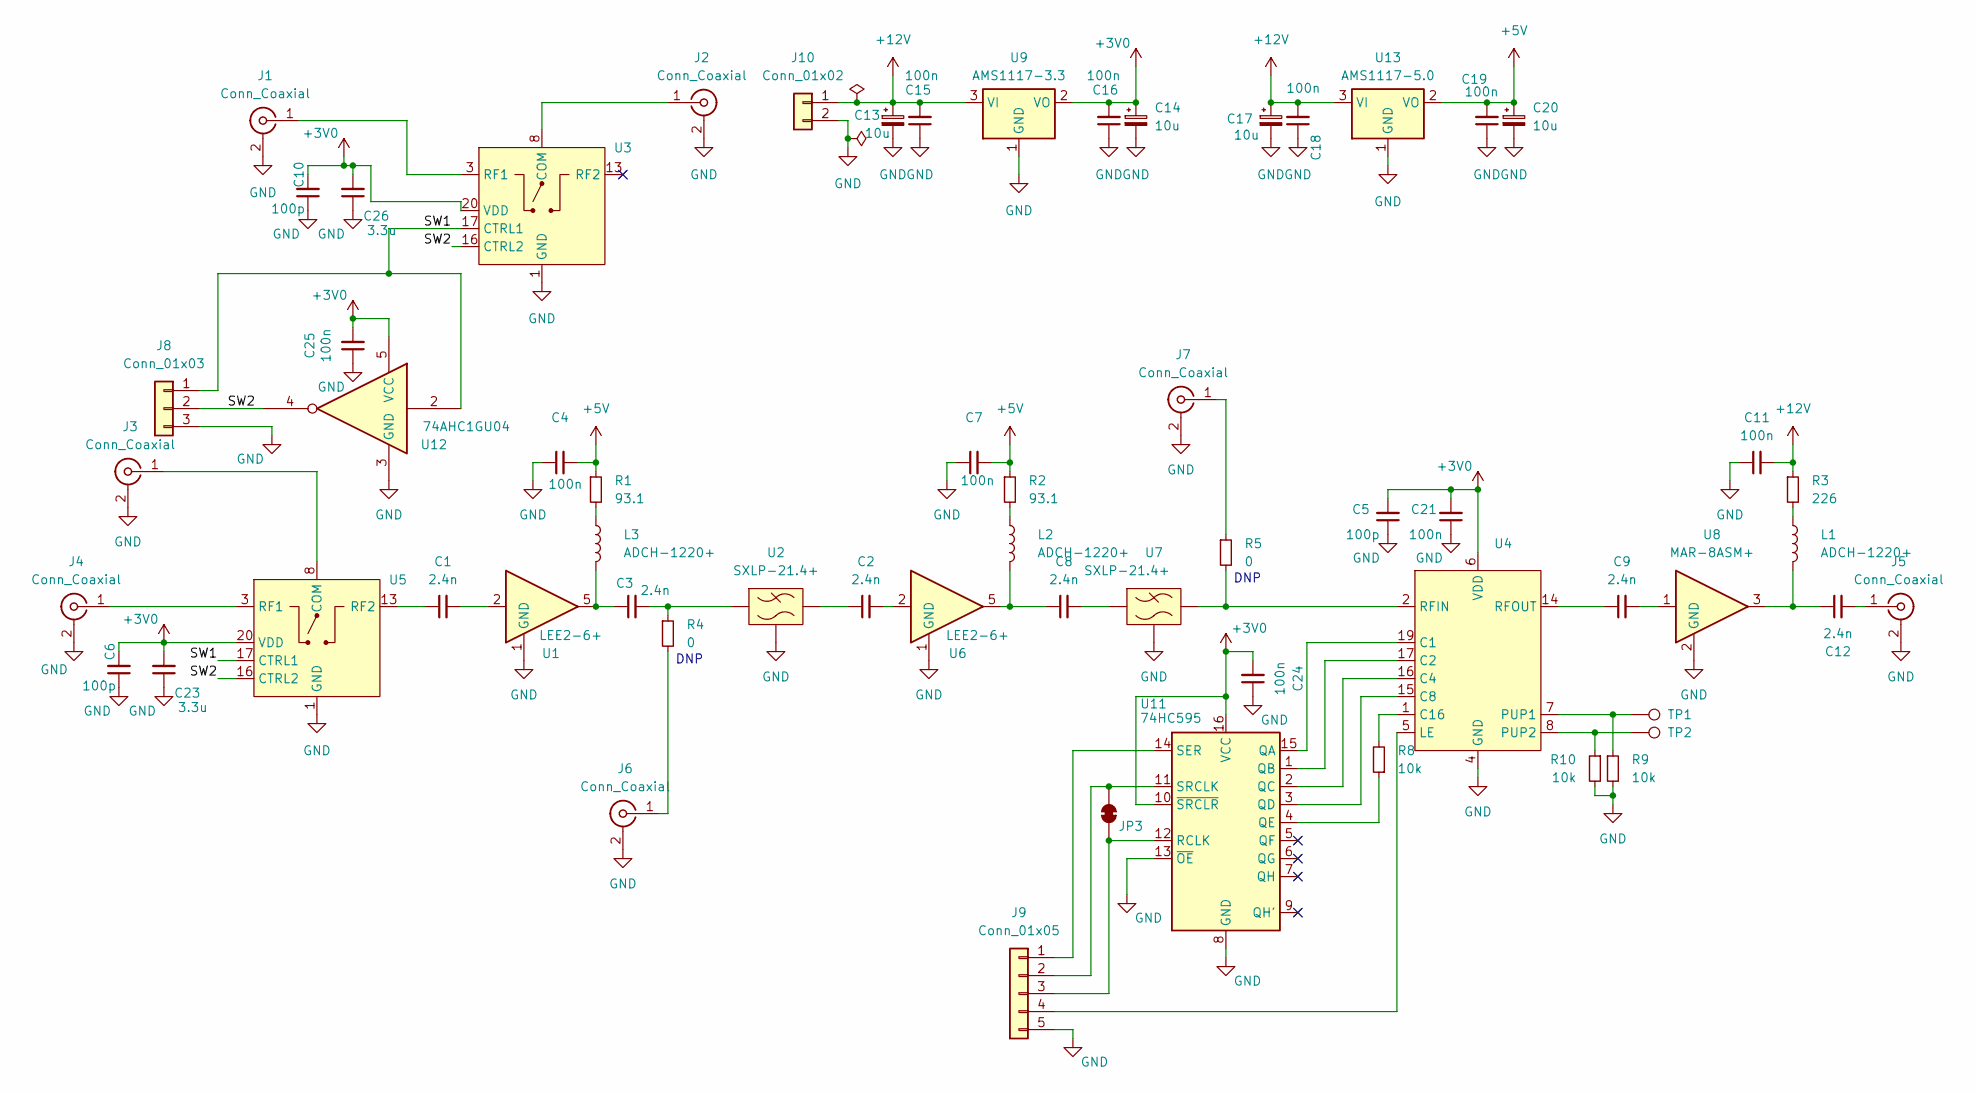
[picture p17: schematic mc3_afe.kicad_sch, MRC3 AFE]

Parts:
C1, C2, C3, C8, C9, C12: 2.4n; C_0805_2012Metric
C4, C7, C11, C21: 100n; C_0805_2012Metric
C5, C6, C10: 100p; C_0603_1608Metric
C13, C14, C17, C20: 10u; C_1206_3216Metric
C15, C16, C18, C19, C24, C25: 100n; C_0603_1608Metric
C23, C26: 3.3u; C_1206_3216Metric
J1, J3, J4, J6, J7: Conn_Coaxial; SMA_Samtec_SMA-J-P-H-ST-EM1_EdgeMount
J2, J5: Conn_Coaxial; MMCX_Molex_73415-1471_Vertical
J8: Conn_01x03; PinHeader_1x03_P2.54mm_Vertical
J9: Conn_01x05; PinHeader_1x05_P2.54mm_Vertical
J10: Conn_01x02; PinHeader_1x02_P2.54mm_Vertical
JP3: SolderJumper_2_Bridged; SolderJumper-2_P1.3mm_Bridged_Pad1.0x1.5mm
L1, L2, L3: ADCH-1220+; Mini-Circuits_CD637_H5.23mm
R1, R2: 93.1; R_0402_1005Metric
R3: 226; R_1206_3216Metric
R4, R5: 0; R_0402_1005Metric
R8, R9, R10: 10k; R_0603_1608Metric
TP1, TP2: TestPoint; TestPoint_THTPad_D1.0mm_Drill0.5mm
U1, U6: LEE2-6+; Mini-Circuits_FG873
U2, U7: SXLP-21.4+; Mini-Circuits_HF1139_LandPatternPL-230
U3, U4, U5: TQFN-20-1EP_4x4mm_P0.5mm_EP2.1x2.1mm
U8: MAR-8ASM+; Mini-Circuits_WW107
U9: AMS1117-3.3; SOT-223-3_TabPin2
U11: 74HC595; DHVQFN-16-1EP_2.5x3.5mm_P0.5mm_EP1x2mm; MPN SN74HCS595
U12: 74AHC1GU04; SOT-353_SC-70-5; MPN MC74VHC1GT04DFT1G
U13: AMS1117-5.0; SOT-223-3_TabPin2

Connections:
+3V0: C5.2, C6.2, C10.2, C14.1, C16.2, C21.2, C23.2, C24.2, C25.2, C26.2, U3.20 (VDD), U4.6 (VDD), U4.9 (VDD), U5.20 (VDD), U9.2 (VO), U11.10 (~SRCLR), U11.16 (VCC), U12.5 (VCC)
+5V: C4.2, C7.2, C19.2, C20.1, R1.1, R2.1, U13.2 (VO)
+12V: C11.2, C13.1, C15.2, C17.1, C18.2, J10.1, R3.1, U9.3 (VI), U13.3 (VI)
/SW1: J8.1, U3.17 (CTRL1), U5.17 (CTRL1), U12.2
/SW2: J8.2, U3.16 (CTRL2), U5.16 (CTRL2), U12.4
GND: C4.1, C5.1, C6.1, C7.1, C10.1, C11.1, C13.2, C14.2, C15.1, C16.1, C17.2, C18.1, C19.1, C20.2, C21.1, C23.1, C24.1, C25.1, C26.1, J1.2 (Ext), J2.2 (Ext), J3.2 (Ext), J4.2 (Ext), J5.2 (Ext), J6.2 (Ext), J7.2 (Ext), J8.3, J9.5, J10.2, R9.2, R10.2, U1.1 (GND), U1.3 (GND), U1.4 (GND), U1.6 (GND), U1.7 (GND), U2.2 (GND), U2.3 (GND), U2.4 (GND), U2.5 (GND), U2.6 (GND), U2.7 (GND), U3.1 (GND), U3.2 (GND), U3.4 (GND), U3.5 (GND), U3.6 (GND), U3.7 (GND), U3.9 (GND), U3.10 (GND), U3.11 (GND), U3.12 (GND), U3.14 (GND), U3.15 (GND), U3.18 (GND), U3.19 (GND), U3.21 (GND), U4.4 (GND), U4.10 (GND), U4.11 (GND), U4.12 (GND), U4.13 (GND), U4.18 (GND), U4.21 (GND), U5.1 (GND), U5.2 (GND), U5.4 (GND), U5.5 (GND), U5.6 (GND), U5.7 (GND), U5.9 (GND), U5.10 (GND), U5.11 (GND), U5.12 (GND), U5.14 (GND), U5.15 (GND), U5.18 (GND), U5.19 (GND), U5.21 (GND), U6.1 (GND), U6.3 (GND), U6.4 (GND), U6.6 (GND), U6.7 (GND), U7.2 (GND), U7.3 (GND), U7.4 (GND), U7.5 (GND), U7.6 (GND), U7.7 (GND), U8.2 (GND), U8.4 (GND), U9.1 (GND), U11.8 (GND), U11.13 (~OE), U12.3 (GND), U13.1 (GND)
unnamed: C1.2, U1.2
unnamed: C2.1, U2.8
unnamed: C2.2, U6.2
unnamed: C3.2, R4.1, U2.1
unnamed: C8.2, U7.1
unnamed: C9.2, U8.1
unnamed: J1.1 (In), U3.3 (RF1)
unnamed: J2.1 (In), U3.8 (COM)
unnamed: J3.1 (In), U5.8 (COM)
unnamed: J4.1 (In), U5.3 (RF1)
unnamed: C12.2, J5.1 (In)
unnamed: J6.1 (In), R4.2
unnamed: J7.1 (In), R5.1
unnamed: J9.1, U11.14 (SER)
unnamed: J9.2, JP3.2 (B), U11.11 (SRCLK)
unnamed: J9.3, JP3.1 (A), U11.12 (RCLK)
unnamed: J9.4, U4.5 (LE)
unnamed: L1.4 (RFGND), R3.2
unnamed: C12.1, L1.1 (RFIN), U8.3
unnamed: L2.4 (RFGND), R2.2
unnamed: C8.1, L2.1 (RFIN), U6.5
unnamed: L3.4 (RFGND), R1.2
unnamed: C3.1, L3.1 (RFIN), U1.5
unnamed: R8.2, U4.1 (C16)
unnamed: R9.1, TP1.1, U4.7 (PUP1)
unnamed: R10.1, TP2.1, U4.8 (PUP2)
unnamed: R5.2, U4.2 (RFIN), U7.8
unnamed: C9.1, U4.14 (RFOUT)
unnamed: C1.1, U5.13 (RF2)
unnamed: U4.19 (C1), U11.15 (QA)
unnamed: U4.17 (C2), U11.1 (QB)
unnamed: U4.16 (C4), U11.2 (QC)
unnamed: U4.15 (C8), U11.3 (QD)
unnamed: R8.1, U11.4 (QE)

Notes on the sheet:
DNP

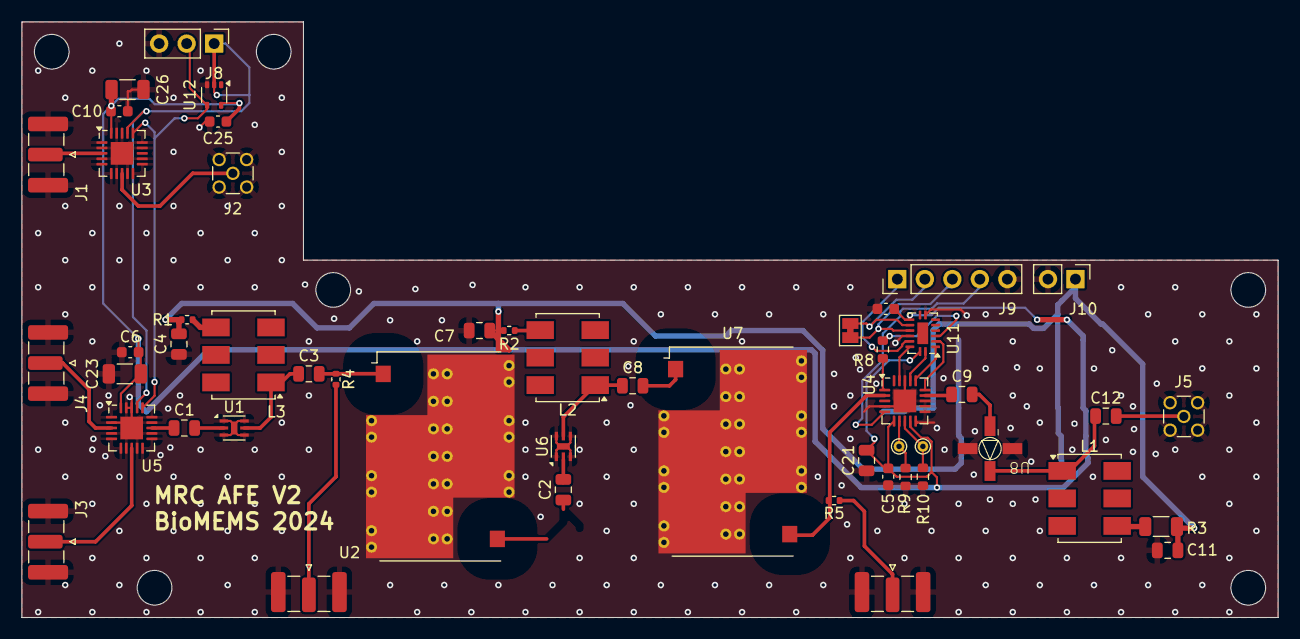
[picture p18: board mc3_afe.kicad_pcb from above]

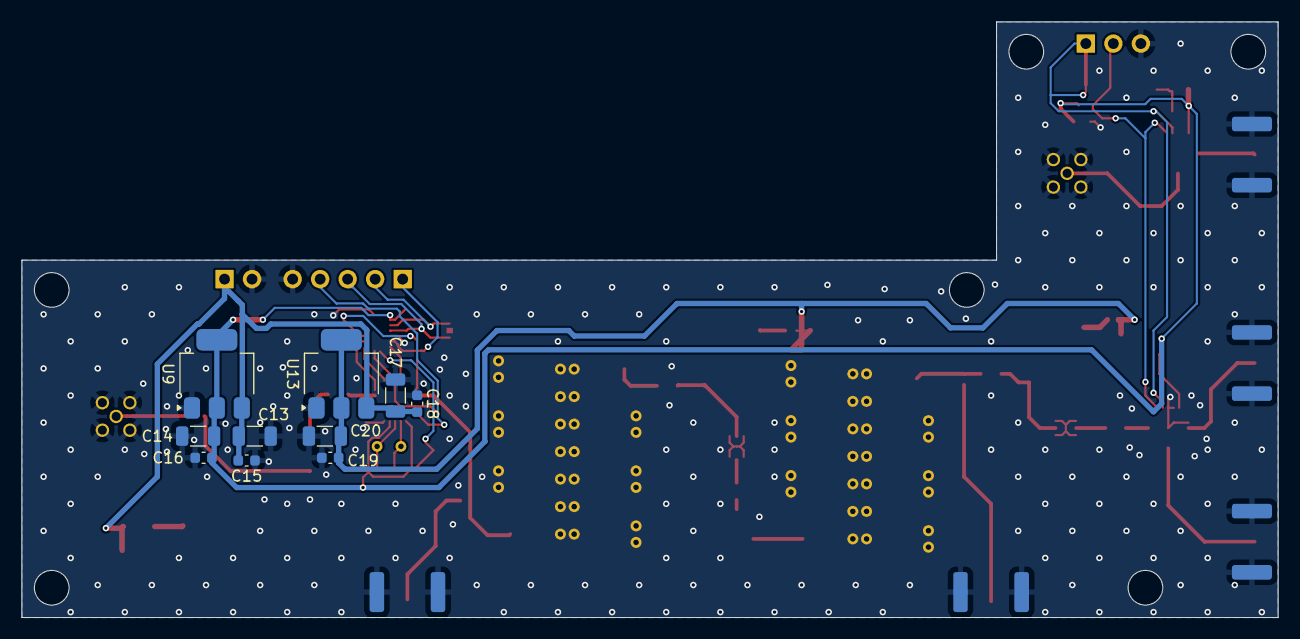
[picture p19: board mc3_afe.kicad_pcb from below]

Board: 4 copper layers, 116.0 x 55.0 mm, 61 parts (10 on the bottom side), 40 nets.

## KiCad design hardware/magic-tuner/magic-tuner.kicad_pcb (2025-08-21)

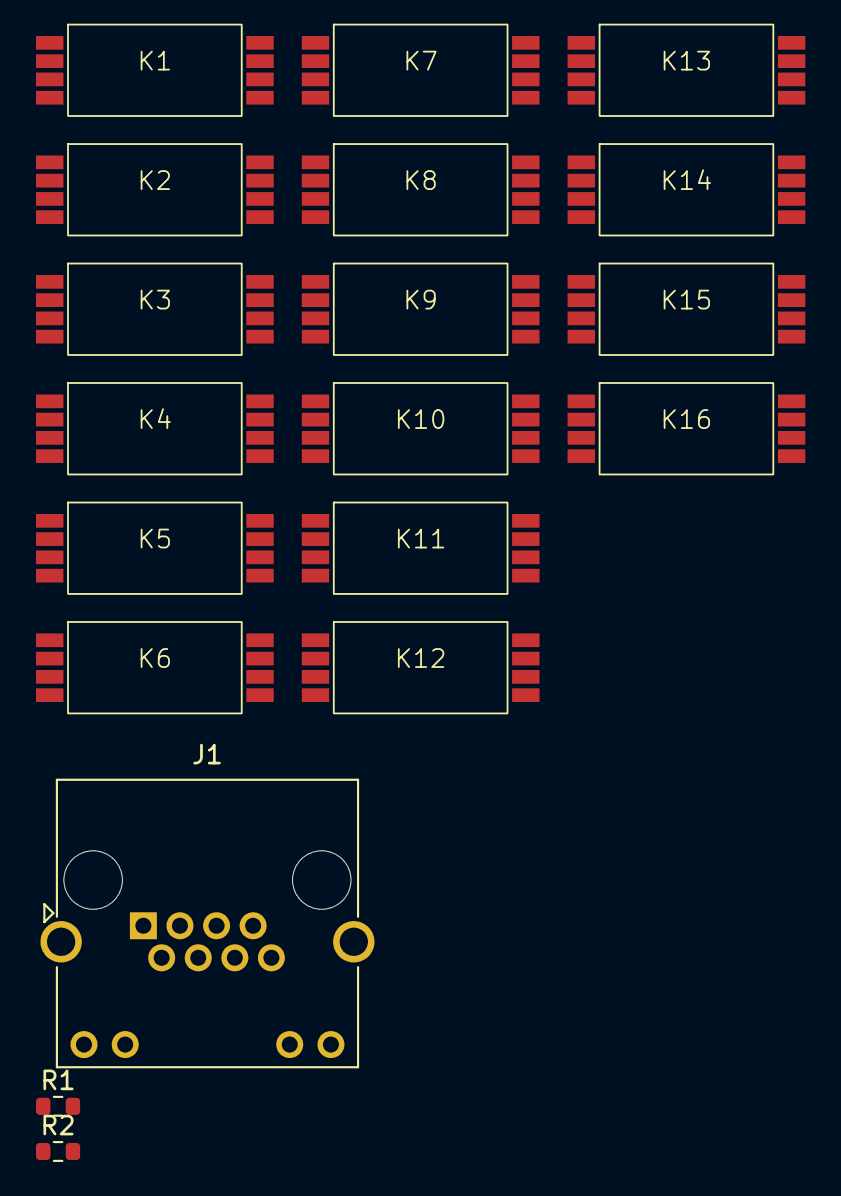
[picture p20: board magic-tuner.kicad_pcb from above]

Board: 2 copper layers, 19 parts (0 on the bottom side), 6 nets, no tracks yet.

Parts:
J1: RJ45_LED_Shielded; RJ45_Amphenol_RJHSE538X
K1, K2, K3, K4, K5, K6, K7, K8, K9, K10, K11, K12, K13, K14, K15, K16: 9814; 9814_Reed_Relay
R1, R2: 4.7k; R_0603_1608Metric

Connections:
/cap_bank/C1: K1.6, K2.6, K3.6, K4.6, K5.6, K6.6, K7.6, K8.6, K9.6, K10.6, K11.6, K12.6, K13.6, K14.6, K15.6, K16.6
/cap_bank/R+: K1.2, K2.2, K3.2, K4.2, K5.2, K6.2, K7.2, K8.2, K9.2, K10.2, K11.2, K12.2, K13.2, K14.2, K15.2, K16.2
/cap_bank/R-: K1.1, K2.1, K3.1, K4.1, K5.1, K6.1, K7.1, K8.1, K9.1, K10.1, K11.1, K12.1, K13.1, K14.1, K15.1, K16.1
GND: J1.1, J1.SH, K1.3 (SH), K1.4, K1.7, K1.8, K2.3 (SH), K2.4, K2.7, K2.8, K3.3 (SH), K3.4, K3.7, K3.8, K4.3 (SH), K4.4, K4.7, K4.8, K5.3 (SH), K5.4, K5.7, K5.8, K6.3 (SH), K6.4, K6.7, K6.8, K7.3 (SH), K7.4, K7.7, K7.8, K8.3 (SH), K8.4, K8.7, K8.8, K9.3 (SH), K9.4, K9.7, K9.8, K10.3 (SH), K10.4, K10.7, K10.8, K11.3 (SH), K11.4, K11.7, K11.8, K12.3 (SH), K12.4, K12.7, K12.8, K13.3 (SH), K13.4, K13.7, K13.8, K14.3 (SH), K14.4, K14.7, K14.8, K15.3 (SH), K15.4, K15.7, K15.8, K16.3 (SH), K16.4, K16.7, K16.8, R1.1, R2.1
unnamed: J1.9, R1.2
unnamed: J1.11, R2.2

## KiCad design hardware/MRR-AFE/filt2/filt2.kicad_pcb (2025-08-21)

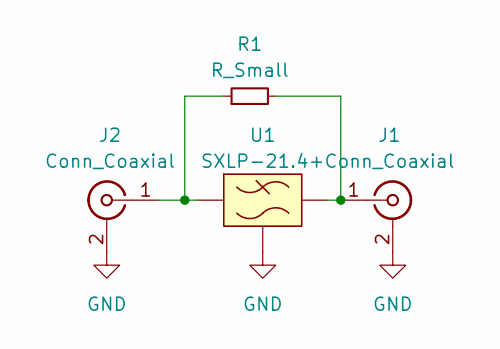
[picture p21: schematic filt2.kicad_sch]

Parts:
J1, J2: Conn_Coaxial; CONSMA013.062-Vertical
R1: R_Small; R_0603_1608Metric
U1: SXLP-21.4+; Mini-Circuits_HF1139_LandPatternPL-230_Truncated

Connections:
GND: J1.2 (Ext), J2.2 (Ext), U1.2 (GND), U1.3 (GND), U1.4 (GND), U1.5 (GND), U1.6 (GND), U1.7 (GND)
unnamed: J1.1 (In), R1.2, U1.8
unnamed: J2.1 (In), R1.1, U1.1

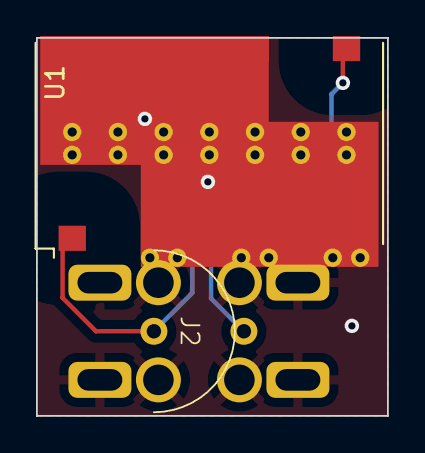
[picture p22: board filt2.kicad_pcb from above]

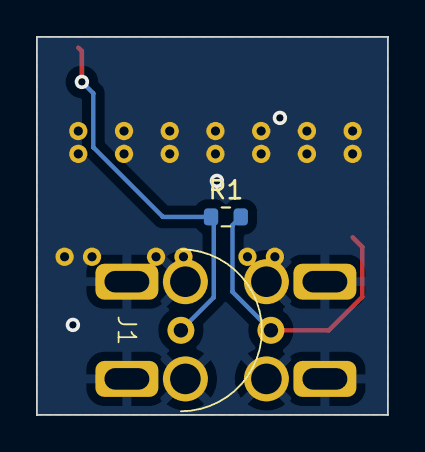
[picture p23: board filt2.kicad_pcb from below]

Board: 2 copper layers, 19.5 x 21.0 mm, 4 parts (2 on the bottom side), 3 nets.

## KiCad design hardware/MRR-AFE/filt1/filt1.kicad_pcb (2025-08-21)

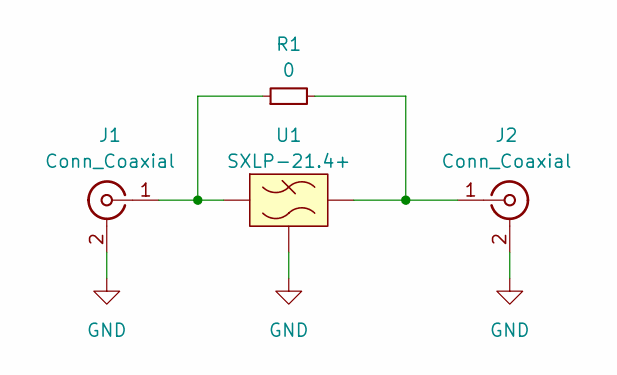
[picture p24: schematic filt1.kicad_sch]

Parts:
J1: Conn_Coaxial; CONSMA013.062-Vertical
J2: Conn_Coaxial; 538-73251-6521
R1: 0; R_0603_1608Metric
U1: SXLP-21.4+; Mini-Circuits_HF1139_LandPatternPL-230_Truncated

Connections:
GND: J1.2 (Ext), J2.2 (Ext), U1.2 (GND), U1.3 (GND), U1.4 (GND), U1.5 (GND), U1.6 (GND), U1.7 (GND)
unnamed: J1.1 (In), R1.1, U1.1
unnamed: J2.1 (In), R1.2, U1.8

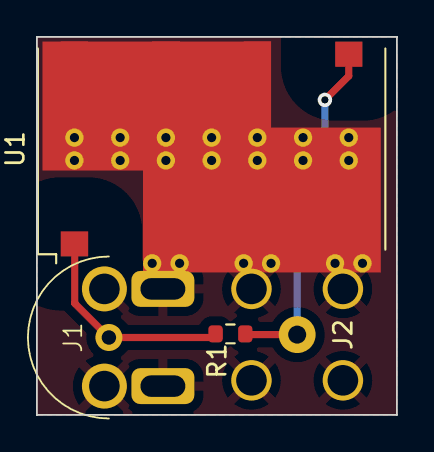
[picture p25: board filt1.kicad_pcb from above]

Board: 2 copper layers, 20.0 x 21.0 mm, 4 parts (1 on the bottom side), 3 nets.

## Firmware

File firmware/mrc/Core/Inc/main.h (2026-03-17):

/* USER CODE BEGIN Header */
/**
  ******************************************************************************
  * @file           : main.h
  * @brief          : Header for main.c file.
  *                   This file contains the common defines of the application.
  ******************************************************************************
  * @attention
  *
  * Copyright (c) 2024 STMicroelectronics.
  * All rights reserved.
  *
  * This software is licensed under terms that can be found in the LICENSE file
  * in the root directory of this software component.
  * If no LICENSE file comes with this software, it is provided AS-IS.
  *
  ******************************************************************************
  */
/* USER CODE END Header */

/* Define to prevent recursive inclusion -------------------------------------*/
#ifndef __MAIN_H
#define __MAIN_H

#ifdef __cplusplus
extern "C" {
#endif

/* Includes ------------------------------------------------------------------*/
#include "stm32f7xx_hal.h"

/* Private includes ----------------------------------------------------------*/
/* USER CODE BEGIN Includes */

/* USER CODE END Includes */

/* Exported types ------------------------------------------------------------*/
/* USER CODE BEGIN ET */

/* USER CODE END ET */

/* Exported constants --------------------------------------------------------*/
/* USER CODE BEGIN EC */

/* USER CODE END EC */

/* Exported macro ------------------------------------------------------------*/
/* USER CODE BEGIN EM */

/* USER CODE END EM */

/* Exported functions prototypes ---------------------------------------------*/
void Error_Handler(void);

/* USER CODE BEGIN EFP */
void DEBUG_PRINT(char * format, ...);
void DmaXferCompleteCallback(DMA_HandleTypeDef *hdma);        // Data Transfer Complete callback
/* USER CODE END EFP */

/* Private defines -----------------------------------------------------------*/
#define MAG_IO0_Pin GPIO_PIN_0
#define MAG_IO0_GPIO_Port GPIOF
#define MAG_IO1_Pin GPIO_PIN_1
#define MAG_IO1_GPIO_Port GPIOF
#define DAC_NRST_Pin GPIO_PIN_2
#define DAC_NRST_GPIO_Port GPIOF
#define DAC_SLEEP_Pin GPIO_PIN_3
#define DAC_SLEEP_GPIO_Port GPIOF
#define DAC_TXEN_Pin GPIO_PIN_4
#define DAC_TXEN_GPIO_Port GPIOF
#define ADC_OF2_Pin GPIO_PIN_8
#define ADC_OF2_GPIO_Port GPIOF
#define ADC_OF1_Pin GPIO_PIN_9
#define ADC_OF1_GPIO_Port GPIOF
#define DAC_SEN_Pin GPIO_PIN_0
#define DAC_SEN_GPIO_Port GPIOC
#define ADC_SEN_Pin GPIO_PIN_4
#define ADC_SEN_GPIO_Port GPIOA
#define FPGA_SEN_Pin GPIO_PIN_1
#define FPGA_SEN_GPIO_Port GPIOB
#define MC_LED1_Pin GPIO_PIN_3
#define MC_LED1_GPIO_Port GPIOG
#define MC_LED2_Pin GPIO_PIN_4
#define MC_LED2_GPIO_Port GPIOG
#define UCIO0_Pin GPIO_PIN_6
#define UCIO0_GPIO_Port GPIOG
#define ATT_SER_Pin GPIO_PIN_7
#define ATT_SER_GPIO_Port GPIOG
#define ATT_LE_Pin GPIO_PIN_8
#define ATT_LE_GPIO_Port GPIOG
#define FIFO_FLAG_Pin GPIO_PIN_11
#define FIFO_FLAG_GPIO_Port GPIOC
#define UCIO3_Pin GPIO_PIN_9
#define UCIO3_GPIO_Port GPIOG
#define UCIO4_Pin GPIO_PIN_10
#define UCIO4_GPIO_Port GPIOG
#define ATT_SRCLK_Pin GPIO_PIN_12
#define ATT_SRCLK_GPIO_Port GPIOG

/* USER CODE BEGIN Private defines */

//status return values
#define SUCCESS	0xFF
#define FAIL 0x00
/* USER CODE END Private defines */

#ifdef __cplusplus
}
#endif

#endif /* __MAIN_H */

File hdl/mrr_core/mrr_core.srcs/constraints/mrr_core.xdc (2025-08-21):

set_property BITSTREAM.GENERAL.COMPRESS TRUE [current_design]
set_property BITSTREAM.CONFIG.CONFIGRATE 6 [current_design]
set_property CONFIG_VOLTAGE 3.3 [current_design]
set_property CFGBVS VCCO [current_design]
set_property BITSTREAM.CONFIG.SPI_32BIT_ADDR NO [current_design]
set_property BITSTREAM.CONFIG.SPI_BUSWIDTH 1 [current_design]
set_property BITSTREAM.CONFIG.SPI_FALL_EDGE YES [current_design]

create_clock -period 8.333 -name FPGA_CLK -waveform {0.000 4.167} [get_ports FPGA_CLK]

set_property -dict {PACKAGE_PIN N14 IOSTANDARD LVCMOS33} [get_ports FPGA_CLK]

set_property -dict { PACKAGE_PIN F5 IOSTANDARD LVCMOS18 } [get_ports { ADC_CLKOUT }]
set_property -dict { PACKAGE_PIN L3 IOSTANDARD LVCMOS18 } [get_ports { ADC_DA[0] }]
set_property -dict { PACKAGE_PIN L2 IOSTANDARD LVCMOS18 } [get_ports { ADC_DA[1] }]
set_property -dict { PACKAGE_PIN K2 IOSTANDARD LVCMOS18 } [get_ports { ADC_DA[2] }]
set_property -dict { PACKAGE_PIN K3 IOSTANDARD LVCMOS18 } [get_ports { ADC_DA[3] }]
set_property -dict { PACKAGE_PIN K1 IOSTANDARD LVCMOS18 } [get_ports { ADC_DA[4] }]
set_property -dict { PACKAGE_PIN K5 IOSTANDARD LVCMOS18 } [get_ports { ADC_DA[5] }]
set_property -dict { PACKAGE_PIN J3 IOSTANDARD LVCMOS18 } [get_ports { ADC_DA[6] }]
set_property -dict { PACKAGE_PIN J1 IOSTANDARD LVCMOS18 } [get_ports { ADC_DA[7] }]
set_property -dict { PACKAGE_PIN J4 IOSTANDARD LVCMOS18 } [get_ports { ADC_DA[8] }]
set_property -dict { PACKAGE_PIN H2 IOSTANDARD LVCMOS18 } [get_ports { ADC_DA[9] }]
set_property -dict { PACKAGE_PIN J5 IOSTANDARD LVCMOS18 } [get_ports { ADC_DA[10] }]
set_property -dict { PACKAGE_PIN H3 IOSTANDARD LVCMOS18 } [get_ports { ADC_DA[11] }]
set_property -dict { PACKAGE_PIN G1 IOSTANDARD LVCMOS18 } [get_ports { ADC_DA[12] }]
set_property -dict { PACKAGE_PIN G2 IOSTANDARD LVCMOS18 } [get_ports { ADC_DA[13] }]
set_property -dict { PACKAGE_PIN H4 IOSTANDARD LVCMOS18 } [get_ports { ADC_DB[0] }]
set_property -dict { PACKAGE_PIN F2 IOSTANDARD LVCMOS18 } [get_ports { ADC_DB[1] }]
set_property -dict { PACKAGE_PIN E1 IOSTANDARD LVCMOS18 } [get_ports { ADC_DB[2] }]
set_property -dict { PACKAGE_PIN F3 IOSTANDARD LVCMOS18 } [get_ports { ADC_DB[3] }]
set_property -dict { PACKAGE_PIN F4 IOSTANDARD LVCMOS18 } [get_ports { ADC_DB[4] }]
set_property -dict { PACKAGE_PIN D1 IOSTANDARD LVCMOS18 } [get_ports { ADC_DB[5] }]
set_property -dict { PACKAGE_PIN E2 IOSTANDARD LVCMOS18 } [get_ports { ADC_DB[6] }]
set_property -dict { PACKAGE_PIN E3 IOSTANDARD LVCMOS18 } [get_ports { ADC_DB[7] }]
set_property -dict { PACKAGE_PIN C1 IOSTANDARD LVCMOS18 } [get_ports { ADC_DB[8] }]
set_property -dict { PACKAGE_PIN D3 IOSTANDARD LVCMOS18 } [get_ports { ADC_DB[9] }]
set_property -dict { PACKAGE_PIN D4 IOSTANDARD LVCMOS18 } [get_ports { ADC_DB[10] }]
set_property -dict { PACKAGE_PIN B1 IOSTANDARD LVCMOS18 } [get_ports { ADC_DB[11] }]
set_property -dict { PACKAGE_PIN B2 IOSTANDARD LVCMOS18 } [get_ports { ADC_DB[12] }]
set_property -dict { PACKAGE_PIN A2 IOSTANDARD LVCMOS18 } [get_ports { ADC_DB[13] }]

set_property -dict { PACKAGE_PIN T7 IOSTANDARD LVCMOS33 } [get_ports { DAC_DA[0] }]
set_property -dict { PACKAGE_PIN P8 IOSTANDARD LVCMOS33 } [get_ports { DAC_DA[1] }]
set_property -dict { PACKAGE_PIN R8 IOSTANDARD LVCMOS33 } [get_ports { DAC_DA[2] }]
set_property -dict { PACKAGE_PIN T8 IOSTANDARD LVCMOS33 } [get_ports { DAC_DA[3] }]
set_property -dict { PACKAGE_PIN P9 IOSTANDARD LVCMOS33 } [get_ports { DAC_DA[4] }]
set_property -dict { PACKAGE_PIN T9 IOSTANDARD LVCMOS33 } [get_ports { DAC_DA[5] }]
set_property -dict { PACKAGE_PIN T10 IOSTANDARD LVCMOS33 } [get_ports { DAC_DA[6] }]
set_property -dict { PACKAGE_PIN R10 IOSTANDARD LVCMOS33 } [get_ports { DAC_DA[7] }]
set_property -dict { PACKAGE_PIN P10 IOSTANDARD LVCMOS33 } [get_ports { DAC_DA[8] }]
set_property -dict { PACKAGE_PIN R11 IOSTANDARD LVCMOS33 } [get_ports { DAC_DA[9] }]
set_property -dict { PACKAGE_PIN P11 IOSTANDARD LVCMOS33 } [get_ports { DAC_DA[10] }]
set_property -dict { PACKAGE_PIN T12 IOSTANDARD LVCMOS33 } [get_ports { DAC_DA[11] }]
set_property -dict { PACKAGE_PIN R12 IOSTANDARD LVCMOS33 } [get_ports { DAC_DA[12] }]
set_property -dict { PACKAGE_PIN T13 IOSTANDARD LVCMOS33 } [get_ports { DAC_DA[13] }]
set_property -dict { PACKAGE_PIN R13 IOSTANDARD LVCMOS33 } [get_ports { DAC_DA[14] }]
set_property -dict { PACKAGE_PIN T14 IOSTANDARD LVCMOS33 } [get_ports { DAC_DA[15] }]
set_property -dict { PACKAGE_PIN R7 IOSTANDARD LVCMOS33 } [get_ports { DAC_DB[0] }]
set_property -dict { PACKAGE_PIN R6 IOSTANDARD LVCMOS33 } [get_ports { DAC_DB[1] }]
set_property -dict { PACKAGE_PIN P6 IOSTANDARD LVCMOS33 } [get_ports { DAC_DB[2] }]
set_property -dict { PACKAGE_PIN T5 IOSTANDARD LVCMOS33 } [get_ports { DAC_DB[3] }]
set_property -dict { PACKAGE_PIN R5 IOSTANDARD LVCMOS33 } [get_ports { DAC_DB[4] }]
set_property -dict { PACKAGE_PIN P5 IOSTANDARD LVCMOS33 } [get_ports { DAC_DB[5] }]
set_property -dict { PACKAGE_PIN T4 IOSTANDARD LVCMOS33 } [get_ports { DAC_DB[6] }]
set_property -dict { PACKAGE_PIN P4 IOSTANDARD LVCMOS33 } [get_ports { DAC_DB[7] }]
set_property -dict { PACKAGE_PIN R3 IOSTANDARD LVCMOS33 } [get_ports { DAC_DB[8] }]
set_property -dict { PACKAGE_PIN T3 IOSTANDARD LVCMOS33 } [get_ports { DAC_DB[9] }]
set_property -dict { PACKAGE_PIN N4 IOSTANDARD LVCMOS33 } [get_ports { DAC_DB[10] }]
set_property -dict { PACKAGE_PIN P3 IOSTANDARD LVCMOS33 } [get_ports { DAC_DB[11] }]
set_property -dict { PACKAGE_PIN T2 IOSTANDARD LVCMOS33 } [get_ports { DAC_DB[12] }]
set_property -dict { PACKAGE_PIN R2 IOSTANDARD LVCMOS33 } [get_ports { DAC_DB[13] }]
set_property -dict { PACKAGE_PIN R1 IOSTANDARD LVCMOS33 } [get_ports { DAC_DB[14] }]
set_property -dict { PACKAGE_PIN N3 IOSTANDARD LVCMOS33 } [get_ports { DAC_DB[15] }]
set_property -dict { PACKAGE_PIN D8 IOSTANDARD LVCMOS33 } [get_ports { DAC_PHSTR }]

set_property -dict { PACKAGE_PIN M2 IOSTANDARD LVCMOS33 } [get_ports { SCK }]
set_property -dict { PACKAGE_PIN L4 IOSTANDARD LVCMOS33 } [get_ports { SDI }]
set_property -dict { PACKAGE_PIN M1 IOSTANDARD LVCMOS33 } [get_ports { SDO }]
set_property -dict { PACKAGE_PIN L5 IOSTANDARD LVCMOS33 } [get_ports { SEN }]

set_property -dict { PACKAGE_PIN A14 IOSTANDARD LVCMOS33 } [get_ports { FMC_ALE }]
set_property -dict { PACKAGE_PIN C13 IOSTANDARD LVCMOS33 } [get_ports { FMC_CLE }]
set_property -dict { PACKAGE_PIN B12 IOSTANDARD LVCMOS33 } [get_ports { FMC_NCE }]
set_property -dict { PACKAGE_PIN B11 IOSTANDARD LVCMOS33 } [get_ports { FMC_NOE }]
set_property -dict { PACKAGE_PIN C11 IOSTANDARD LVCMOS33 } [get_ports { FMC_NWE }]
set_property -dict { PACKAGE_PIN B14 IOSTANDARD LVCMOS33 } [get_ports { FSMC_D[0] }]
set_property -dict { PACKAGE_PIN C14 IOSTANDARD LVCMOS33 } [get_ports { FSMC_D[1] }]
set_property -dict { PACKAGE_PIN A12 IOSTANDARD LVCMOS33 } [get_ports { FSMC_D[2] }]
set_property -dict { PACKAGE_PIN C12 IOSTANDARD LVCMOS33 } [get_ports { FSMC_D[3] }]
set_property -dict { PACKAGE_PIN C8 IOSTANDARD LVCMOS33 } [get_ports { FSMC_D[4] }]
set_property -dict { PACKAGE_PIN A8 IOSTANDARD LVCMOS33 } [get_ports { FSMC_D[5] }]
set_property -dict { PACKAGE_PIN C9 IOSTANDARD LVCMOS33 } [get_ports { FSMC_D[6] }]
set_property -dict { PACKAGE_PIN D9 IOSTANDARD LVCMOS33 } [get_ports { FSMC_D[7] }]
set_property -dict { PACKAGE_PIN A9 IOSTANDARD LVCMOS33 } [get_ports { FSMC_D[8] }]
set_property -dict { PACKAGE_PIN B9 IOSTANDARD LVCMOS33 } [get_ports { FSMC_D[9] }]
set_property -dict { PACKAGE_PIN B10 IOSTANDARD LVCMOS33 } [get_ports { FSMC_D[10] }]
set_property -dict { PACKAGE_PIN A10 IOSTANDARD LVCMOS33 } [get_ports { FSMC_D[11] }]
set_property -dict { PACKAGE_PIN E12 IOSTANDARD LVCMOS33 } [get_ports { FSMC_D[12] }]
set_property -dict { PACKAGE_PIN D13 IOSTANDARD LVCMOS33 } [get_ports { FSMC_D[13] }]
set_property -dict { PACKAGE_PIN A13 IOSTANDARD LVCMOS33 } [get_ports { FSMC_D[14] }]
set_property -dict { PACKAGE_PIN E13 IOSTANDARD LVCMOS33 } [get_ports { FSMC_D[15] }]

set_property -dict { PACKAGE_PIN A7 IOSTANDARD LVCMOS18 } [get_ports { GRINX[0] }]
set_property -dict { PACKAGE_PIN B6 IOSTANDARD LVCMOS18 } [get_ports { GRINX[1] }]
set_property -dict { PACKAGE_PIN B5 IOSTANDARD LVCMOS18 } [get_ports { GRINY[0] }]
set_property -dict { PACKAGE_PIN A5 IOSTANDARD LVCMOS18 } [get_ports { GRINY[1] }]
set_property -dict { PACKAGE_PIN A4 IOSTANDARD LVCMOS18 } [get_ports { GRINZ[0] }]
set_property -dict { PACKAGE_PIN B4 IOSTANDARD LVCMOS18 } [get_ports { GRINZ[1] }]

set_property -dict { PACKAGE_PIN B7 IOSTANDARD LVCMOS18 } [get_ports { IO[0] }]
set_property -dict { PACKAGE_PIN H5 IOSTANDARD LVCMOS18 } [get_ports { IO[1] }]
set_property -dict { PACKAGE_PIN N9 IOSTANDARD LVCMOS33 } [get_ports { IO[2] }]
set_property -dict { PACKAGE_PIN M4 IOSTANDARD LVCMOS33 } [get_ports { IO[3] }]
set_property -dict { PACKAGE_PIN M6 IOSTANDARD LVCMOS33 } [get_ports { IO[4] }]
set_property -dict { PACKAGE_PIN M5 IOSTANDARD LVCMOS33 } [get_ports { IO[5] }]
set_property -dict { PACKAGE_PIN E6 IOSTANDARD LVCMOS18 } [get_ports { IO[6] }]

set_property -dict { PACKAGE_PIN G4 IOSTANDARD LVCMOS18 } [get_ports { SW[0] }]
set_property -dict { PACKAGE_PIN H1 IOSTANDARD LVCMOS18 } [get_ports { SW[1] }]
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

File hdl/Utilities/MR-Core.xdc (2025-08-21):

set_property -dict { PACKAGE_PIN N14 IOSTANDARD LVCMOS18 } [get_ports { FPGA_CLK+ }]
set_property -dict { PACKAGE_PIN P14 IOSTANDARD LVCMOS18 } [get_ports { FPGA_CLK- }]

set_property -dict { PACKAGE_PIN E12 IOSTANDARD LVCMOS18 } [get_ports { ADC_CLKOUT }]
set_property -dict { PACKAGE_PIN P1 IOSTANDARD LVCMOS18 } [get_ports { ADC_DA[0] }]
set_property -dict { PACKAGE_PIN N2 IOSTANDARD LVCMOS18 } [get_ports { ADC_DA[1] }]
set_property -dict { PACKAGE_PIN L5 IOSTANDARD LVCMOS18 } [get_ports { ADC_DA[2] }]
set_property -dict { PACKAGE_PIN N1 IOSTANDARD LVCMOS18 } [get_ports { ADC_DA[3] }]
set_property -dict { PACKAGE_PIN M2 IOSTANDARD LVCMOS18 } [get_ports { ADC_DA[4] }]
set_property -dict { PACKAGE_PIN L3 IOSTANDARD LVCMOS18 } [get_ports { ADC_DA[5] }]
set_property -dict { PACKAGE_PIN M1 IOSTANDARD LVCMOS18 } [get_ports { ADC_DA[6] }]
set_property -dict { PACKAGE_PIN L2 IOSTANDARD LVCMOS18 } [get_ports { ADC_DA[7] }]
set_property -dict { PACKAGE_PIN L4 IOSTANDARD LVCMOS18 } [get_ports { ADC_DA[8] }]
set_property -dict { PACKAGE_PIN K2 IOSTANDARD LVCMOS18 } [get_ports { ADC_DA[9] }]
set_property -dict { PACKAGE_PIN K1 IOSTANDARD LVCMOS18 } [get_ports { ADC_DA[10] }]
set_property -dict { PACKAGE_PIN K3 IOSTANDARD LVCMOS18 } [get_ports { ADC_DA[11] }]
set_property -dict { PACKAGE_PIN K5 IOSTANDARD LVCMOS18 } [get_ports { ADC_DA[12] }]
set_property -dict { PACKAGE_PIN J1 IOSTANDARD LVCMOS18 } [get_ports { ADC_DA[13] }]
set_property -dict { PACKAGE_PIN J3 IOSTANDARD LVCMOS18 } [get_ports { ADC_DB[0] }]
set_property -dict { PACKAGE_PIN J4 IOSTANDARD LVCMOS18 } [get_ports { ADC_DB[1] }]
set_property -dict { PACKAGE_PIN H1 IOSTANDARD LVCMOS18 } [get_ports { ADC_DB[2] }]
set_property -dict { PACKAGE_PIN H3 IOSTANDARD LVCMOS18 } [get_ports { ADC_DB[3] }]
set_property -dict { PACKAGE_PIN H4 IOSTANDARD LVCMOS18 } [get_ports { ADC_DB[4] }]
set_property -dict { PACKAGE_PIN G1 IOSTANDARD LVCMOS18 } [get_ports { ADC_DB[5] }]
set_property -dict { PACKAGE_PIN G2 IOSTANDARD LVCMOS18 } [get_ports { ADC_DB[6] }]
set_property -dict { PACKAGE_PIN G4 IOSTANDARD LVCMOS18 } [get_ports { ADC_DB[7] }]
set_property -dict { PACKAGE_PIN F2 IOSTANDARD LVCMOS18 } [get_ports { ADC_DB[8] }]
set_property -dict { PACKAGE_PIN F3 IOSTANDARD LVCMOS18 } [get_ports { ADC_DB[9] }]
set_property -dict { PACKAGE_PIN E1 IOSTANDARD LVCMOS18 } [get_ports { ADC_DB[10] }]
set_property -dict { PACKAGE_PIN F4 IOSTANDARD LVCMOS18 } [get_ports { ADC_DB[11] }]
set_property -dict { PACKAGE_PIN E2 IOSTANDARD LVCMOS18 } [get_ports { ADC_DB[12] }]
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

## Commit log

2025-08-21 Publish MR-Core
    [MR-Core-B_Cu.gbr, MR-Core-B_Mask.gbr, MR-Core-B_Paste.gbr, MR-Core-B_Silkscreen.gbr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]
2025-11-11 well scanning, AFE
    [MR-Core.kicad_sch, mc3_afe-B_Cu.gbr, mc3_afe-B_Mask.gbr, mc3_afe-B_Paste.gbr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]
2026-01-27 Update KiCAD Version, Integrate Libraries
    [MR-Core.kicad_sch, mrc-fpga-config.kicad_sch, mrc-gradient.kicad_sch, mrc-magnet-interface.kicad_sch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]
2026-01-27 Add assembly guide
2026-01-27 Clean bill of materials
    [MR-Core.kicad_sch, MR-Core.ods, MR-Core.xlsx, mrc-fpga-config.kicad_sch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]
2026-01-28 Move assembly instructions
2026-01-28 Fix Assembly.md Photo references
